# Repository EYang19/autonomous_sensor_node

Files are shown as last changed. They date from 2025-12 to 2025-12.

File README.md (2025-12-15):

# Autonomous Sensor Node Design

## Course Project – Group 6

### Team Members
- Chengyu Yang  
- Arno Liu  
- Shijia Liu  
- Zheyang Zheng  

---

## Project Overview

This project focuses on the design and implementation of **autonomous sensor nodes** capable of long-term operation using onboard power supplies. The sensor nodes are designed to independently acquire, process, and transmit sensor data, targeting applications in wearable, industrial, and medical electronics.

Two types of sensor nodes were developed in this project:
- **Photoplethysmography (PPG) Sensor Node**
- **Accelerometer (ACC) Sensor Node**

Each sensor node integrates sensing elements, power management, and a microcontroller unit (MCU) with its peripheral circuitry.

---

## Project Objectives

- Design complete sensor node hardware, including schematic and PCB layout  
- Implement low-power power management and dual-path power supply  
- Integrate MCU, sensors, and peripheral circuits  
- Verify functionality through prototype assembly and testing  
- Characterise sensor performance and validate signal acquisition  

---

## Repository Structure

```text
.
├── Datasheet_tech notes/
│   └── Datasheets and technical notes for key components
│
├── PCB_design/
│   └── Early PCB design files created using KiCad.
│       This folder contains the initial PCB design iterations
│       before the project was migrated to EasyEDA.
│
├── Final PCB Design using Easy EDA/
│   └── Finalised PCB schematics and layout designed in EasyEDA.
│       All later revisions and manufacturing-ready files are
│       maintained in this directory.
│
├── Labbook/
│   └── Laboratory notes, testing logs, and debugging records
│
├── autonomous_sensor_code/
│   └── PPGtest/
│       └── Firmware and test code for the PPG sensor node
│
├── Idea on components selection
│   └── Early design notes and rationale for component selection
│
├── ppg_processed_data.csv
│   └── Processed PPG measurement data used for analysis
│
├── README.md
│   └── Project overview and objectives
│
├── .gitattributes
│   └── Git configuration file
│
└── .DS_Store
    └── System file (can be ignored)

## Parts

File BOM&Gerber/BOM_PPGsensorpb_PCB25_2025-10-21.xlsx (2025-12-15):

No. | Quantity | Comment | Designator | Footprint | Value
1 | 2 | 2450AT18A100E | AE1,AE50 | ANT-SMD_L3.2-W1.6 |  | farnell | yes
2 | 5 | 100nF | C1,C5,C9,C10,C13 | C0603 | 100nF | farnell | yes
3 | 16 | 1uF | C3,C4,C14,C15,C19,C20,C23,C25,C52,C53,C59,C62,C64,C65,C69,C70 | C0603 | 1uF | farnell | yes
4 | 6 | 47uF | C6,C7,C27,C51,C54,C61 | C0805 | 47uF | farnell | yes
5 | 2 | 10uF | C12,C67 | C0603 | 10uF | farnell | yes
6 | 2 | 10nF | C16,C63 | C0603 | 10nF | farnell | yes
7 | 2 | 1pF | C17,C66 | C0201 | 1pF | farnell | yes
8 | 4 | 20pF | C21,C22,C56,C58 | C0603 | 20pF | farnell | yes
9 | 3 | 0Ω | C26,R14,R60 | R0603 | 0Ω | farnell | yes
10 | 5 | 100nF | C50,C55,C57,C60,C68 | C0402 | 100nF | farnell | yes
11 | 2 | B5819W-TP | D1,D50 | SOD-123_L2.8-W1.8-LS3.7-RD |  | farnell | yes
12 | 2 | PZ254V-11-04P | H1,H50 | HDR-TH_4P-P2.54-V-M |  | nonneed
13 | 2 | 2nH | L1,L50 | L0402 | 2nH | farnell | yes
14 | 2 | 3.9nH | L2,L51 | L0201 | 3.9nH | farnell | yes
15 | 2 | 2.7nH | L3,L52 | L0201 | 2.7nH | farnell | yes
16 | 1 | DNP | L4 | L0603 | tbc
17 | 6 | LTST-C190KSKT | LED1,LED2,LED3,LED50,LED51,LED52 | LED0603-RD |  | farnell | yes
18 | 2 | AO3407A | Q1,Q52 | SOT-23-3_L2.9-W1.6-P1.90-LS2.8-BR |  | alt farnell(DMG2305UX) | yes
19 | 2 | DW01 | Q2,Q51 | SOT-23-6_L2.9-W1.6-P0.95-LS2.8-BR |  | alt farnell(AP9101C) | yes
20 | 2 | 8205A | Q3,Q50 | SOT-23-6_L2.9-W1.6-P0.95-LS2.8-BR |  | digiikey | yes
21 | 14 | 10kΩ | R1,R2,R4,R7,R9,R10,R11,R50,R54,R55,R61,R62,R64,R66 | R0603 | 10kΩ | farnell | yes
22 | 2 | 100Ω | R3,R58 | R0603 | 100Ω | farnell | yes
23 | 2 | 1.5kΩ | R5,R51 | R0603 | 1.5kΩ | farnell | yes
24 | 2 | 1kΩ | R6,R52 | R0603 | 1kΩ | farnell | yes
25 | 6 | 4.7kΩ | R8,R12,R13,R59,R63,R65 | R0603 | 4.7kΩ | farnell | yes
26 | 4 | 100kΩ | R18,R19,R56,R57 | R0603 | 100kΩ | farnell | yes
27 | 2 | 3kΩ | R20,R53 | R0603 | 3kΩ | farnell | yes
28 | 2 | MSK12C02 | SW1,SW50 | SW-TH_MSK12C02 |  | farnell alt(4125522) | yes
29 | 4 | TS-1088-AR02016 | SW2,SW3,SW51,SW52 | SW-SMD_L3.9-W3.0-P4.45 |  | farnell alt(2908777) | yes
30 | 2 | MAX17048G+T10 | U1,U53 | TDFN-8_L2.0-W2.0-P0.50-BL-EP1.2 | y | farnell | yes
31 | 2 | TLV75533PDBVR | U2,U51 | SOT-23-5_L3.0-W1.7-P0.95-LS2.8-BR |  | mouser | yes
32 | 2 | TPS22917DBVR | U3,U50 | SOT-23-6_L2.9-W1.6-P0.95-LS2.8-BR |  | farnell | yes
33 | 2 | SMTU2477N-LF | U5,U54 | BAT-SMD_SMTU2477N-LF |  | mouser | yes
34 | 2 | LTC4412ES6#TRPBF | U6,U52 | TSOT-23-6_L2.9-W1.6-P0.95-LS2.8-BR |  | farnell | yes
35 | 2 | ESP32-C3FH4 | U7,U55 | QFN-32_L5.0-W5.0-P0.50-TL-EP3.7 |  | mouser | yes
36 | 2 | MAX30102EFD+T | U8,U57 | OESIP-14_L5.6-W3.3-P0.80-TL |  | farnell | yes
37 | 2 | TPS78218DDCR | U9,U56 | SOT-23-5_L3.0-W1.7-P0.95-LS2.8-BR |  |  | yes
38 | 2 | 40MHz | X1,X50 | OSC-SMD_4P-L3.2-W2.5-BL_SIT8008BI | 40MHz | farnell | yes

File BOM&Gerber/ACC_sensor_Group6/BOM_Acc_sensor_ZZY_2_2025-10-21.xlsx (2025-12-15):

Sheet: bom模板
 |  |  |  | Bill of Materials | BOM_Acc_sensor_ZZY_2_Acc_sensor_ZZY_2_2025-10-21
 |  |  |  | Project Title： | Sensor_node
 |  |  |  | Variant:
 |  |  |  | Report Time： | 2025/Oct/21 23:57:43
No. | Quantity | Comment | Designator | Footprint | Value | Manufacturer Part | Manufacturer | Supplier Part | Supplier | LCSC Price | Total
1 | 2 | 2450AT18A100E | AE1, AE2 | ANT-SMD_L3.2-W1.6 |  | 2450AT18A100E | JOHANSON(约翰逊) | C89334 | LCSC |  | #VALUE!
2 | 14 | 100nF | C1, C2, C5, C9, C10, C13, C26, C42, C43, C47, C48, C49, C50, C51 | C0603 | 100nF | CC0603KRX7R9BB104 | YAGEO(国巨) | C14663 | LCSC |  | #VALUE!
3 | 12 | 1uF | C3, C4, C14, C15, C19, C20, C34, C35, C36, C37, C38, C39 | C0603 | 1uF | CL10A105KB8NNNC | SAMSUNG(三星) | C15849 | LCSC |  | #VALUE!
4 | 6 | 47uF | C6, C7, C8, C29, C30, C31 | C0805 | 47uF | CL21A476MQYNNNE | SAMSUNG(三星) | C16780 | LCSC |  | #VALUE!
5 | 4 | 10uF | C12, C27, C44, C45 | C0603 | 10uF | CL10A106KP8NNNC | SAMSUNG(三星) | C19702 | LCSC |  | #VALUE!
6 | 2 | 10nF | C16, C32 | C0603 | 10nF | 0603B103K500NT | FH(风华) | C57112 | LCSC |  | #VALUE!
7 | 1 | 1pF | C17 | L0201 | 1pF | GRM0335C1H1R0BA01D | muRata(村田) | C85893 | LCSC |  | #VALUE!
8 | 4 | 20pF | C21, C22, C40, C41 | C0603 | 20pF | CL10C200JB8NNNC | SAMSUNG(三星) | C1648 | LCSC |  | #VALUE!
9 | 1 | 0 | C28 | C0603 | 0 | CL10A106KP8NNNC | SAMSUNG(三星) |  | LCSC |  | #VALUE!
10 | 1 | 1pF | C33 | C0201 | 1pF | GRM0335C1H1R0BA01D | muRata(村田) | C85893 | LCSC |  | #VALUE!
11 | 1 | 0Ω | C46 | C0603 | 0Ω | 0603WAF0000T5E | UNI-ROYAL(厚声) | C21189 | LCSC |  | #VALUE!
12 | 2 | B5819W-TP | D1, D2 | SOD-123_L2.8-W1.8-LS3.7-RD |  | B5819W-TP | MCC(美微科) | C84354 | LCSC |  | #VALUE!
13 | 2 | PZ254V-11-04P | H1, H2 | HDR-TH_4P-P2.54-V-M |  | PZ254V-11-04P | XFCN(兴飞) | C2691448 | LCSC |  | #VALUE!
14 | 2 | 2nH | L1, L6 | L0603 | 2nH | SDCL1608C2N0STDF | Sunlord(顺络) | C370234 | LCSC |  | #VALUE!
15 | 2 | 3.9nH | L2, L7 | L0201 | 3.9nH | LQP03HQ3N9B02D | muRata(村田) | C337939 | LCSC |  | #VALUE!
16 | 2 | 2.7nH | L3, L8 | L0201 | 2.7nH | LQP03HQ2N7B02D | muRata(村田) | C7216765 | LCSC |  | #VALUE!
17 | 1 | 0 | L4 | L0603 | 0 | SDCL1608C2N0STDF | Sunlord(顺络) |  | LCSC |  | #VALUE!
18 | 1 | Device_L | L5 | L0603 |  |  |  |  |  |  | #VALUE!
19 | 6 | LTST-C190KSKT | LED1, LED2, LED3, LED4, LED5, LED6 | LED0603-RD |  | LTST-C190KSKT | LITEON(光宝) | C125095 | LCSC |  | #VALUE!
20 | 2 | AO3407A | Q1, Q6 | SOT-23-3_L2.9-W1.6-P1.90-LS2.8-BR |  | AO3407A | AOS | C15155 | LCSC |  | #VALUE!
21 | 2 | DW01 | Q2, Q4 | SOT-23-6_L2.9-W1.6-P0.95-LS2.8-BR |  | DW01 | Hottech(合科泰) | C181096 | LCSC |  | #VALUE!
22 | 2 | 8205A | Q3, Q5 | SOT-23-6_L2.9-W1.6-P0.95-LS2.8-BR |  | 8205A | JSMSEMI(杰盛微) | C2762931 | LCSC |  | #VALUE!
23 | 14 | 10kΩ | R1, R2, R4, R7, R9, R10, R11, R27, R28, R29, R30, R31, R32, R33 | R0603 | 10kΩ | 0603WAF1002T5E | UNI-ROYAL(厚声) | C25804 | LCSC |  | #VALUE!
24 | 2 | 100Ω | R3, R24 | R0603 | 100Ω | 0603WAF1000T5E | UNI-ROYAL(厚声) | C22775 | LCSC |  | #VALUE!
25 | 2 | 1.5kΩ | R5, R25 | R0603 | 1.5kΩ | 0603WAF1501T5E | UNI-ROYAL(厚声) | C22843 | LCSC |  | #VALUE!
26 | 2 | 1kΩ | R6, R26 | R0603 | 1kΩ | 0603WAF1001T5E | UNI-ROYAL(厚声) | C21190 | LCSC |  | #VALUE!
27 | 6 | 4.7kΩ | R8, R12, R13, R34, R35, R36 | R0603 | 4.7kΩ | 0603WAF4701T5E | UNI-ROYAL(厚声) | C23162 | LCSC |  | #VALUE!
28 | 2 | 0Ω | R14, R37 | R0603 | 0Ω | 0603WAF0000T5E | UNI-ROYAL(厚声) | C21189 | LCSC |  | #VALUE!
29 | 4 | 100kΩ | R18, R19, R38, R39 | R0603 | 100kΩ | 0603WAF1003T5E | UNI-ROYAL(厚声) | C25803 | LCSC |  | #VALUE!
30 | 2 | 3kΩ | R20, R40 | R0603 | 3kΩ | 0603WAF3001T5E | UNI-ROYAL(厚声) | C4211 | LCSC |  | #VALUE!
31 | 6 | 22Ω | R21, R22, R23, R41, R42, R43 | R0603 | 22Ω | 0603WAF220JT5E | UNI-ROYAL(厚声) | C23345 | LCSC |  | #VALUE!
32 | 2 | MSK12C02 | SW1, SW4 | SW-TH_MSK12C02 |  | MSK12C02 | SHOU HAN(首韩) | C431540 | LCSC |  | #VALUE!
33 | 4 | TS-1088-AR02016 | SW2, SW3, SW5, SW6 | SW-SMD_L3.9-W3.0-P4.45 |  | TS-1088-AR02016 | XUNPU(讯普) | C720477 | LCSC |  | #VALUE!
34 | 2 | MAX17048G+T10 | U1, U10 | TDFN-8_L2.0-W2.0-P0.50-BL-EP1.2 |  | MAX17048G+T10 | ADI(亚德诺)/MAXIM(美信) | C2682616 | LCSC |  | #VALUE!
35 | 2 | TLV75533PDBVR | U2, U13 | SOT-23-5_L3.0-W1.7-P0.95-LS2.8-BR |  | TLV75533PDBVR | TI(德州仪器) | C404027 | LCSC |  | #VALUE!
36 | 2 | TPS22917DBVR | U3, U12 | SOT-23-6_L2.9-W1.6-P0.95-LS2.8-BR |  | TPS22917DBVR | TI(德州仪器) | C2681320 | LCSC |  | #VALUE!
37 | 2 | LIS2DE12TR | U4, U8 | LGA-12_L2.0-W2.0-P0.50-BL |  | LIS2DE12TR | ST(意法半导体) | C155639 | LCSC |  | #VALUE!
38 | 2 | SMTU2477N-LF | U5, U9 | BAT-SMD_SMTU2477N-LF |  | SMTU2477N-LF | RENATA(瑞纳达) | C3029193 | LCSC |  | #VALUE!
39 | 2 | LTC4412ES6#TRPBF | U6, U11 | TSOT-23-6_L2.9-W1.6-P0.95-LS2.8-BR |  | LTC4412ES6#TRPBF | ADI(亚德诺) | C514442 | LCSC |  | #VALUE!
40 | 1 | ESP32-C3 | U7 | QFN-32_L5.0-W5.0-P0.50-TL-EP3.7 |  | ESP32-C3 | ESPRESSIF(乐鑫) | C2838500 | LCSC |  | #VALUE!
41 | 1 | ESP32-C3FH4 | U14 | QFN-32_L5.0-W5.0-P0.50-TL-EP3.7 |  | ESP32-C3FH4 | ESPRESSIF(乐鑫) | C2858491 | LCSC |  | #VALUE!
42 | 2 | 40MHz | X1, X2 | OSC-SMD_4P-L3.2-W2.5-BL_SIT8008BI | 40MHz | X322540MPB4SI | YXC(扬兴晶振) | C9010 | LCSC |  | #VALUE!
43 | #VALUE!

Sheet: Field汇总
Project Title | Sensor_node
Borard Title | Acc_sensor_ZZY_2
Schematic Title | Acc_sensor_ZZY_2
PCB Title
Variant Name
Total Quantity | 134
Report Time | 23:57:43
Report Date | 2025年10月21日
Report Date&Time | 2025年10月21日 23:57:43
File Name | BOM_Acc_sensor_ZZY_2_Acc_sensor_ZZY_2_2025-10-21
Filter Option | Add into BOM:no;

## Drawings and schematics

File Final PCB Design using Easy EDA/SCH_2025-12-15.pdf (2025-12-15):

# Power Management

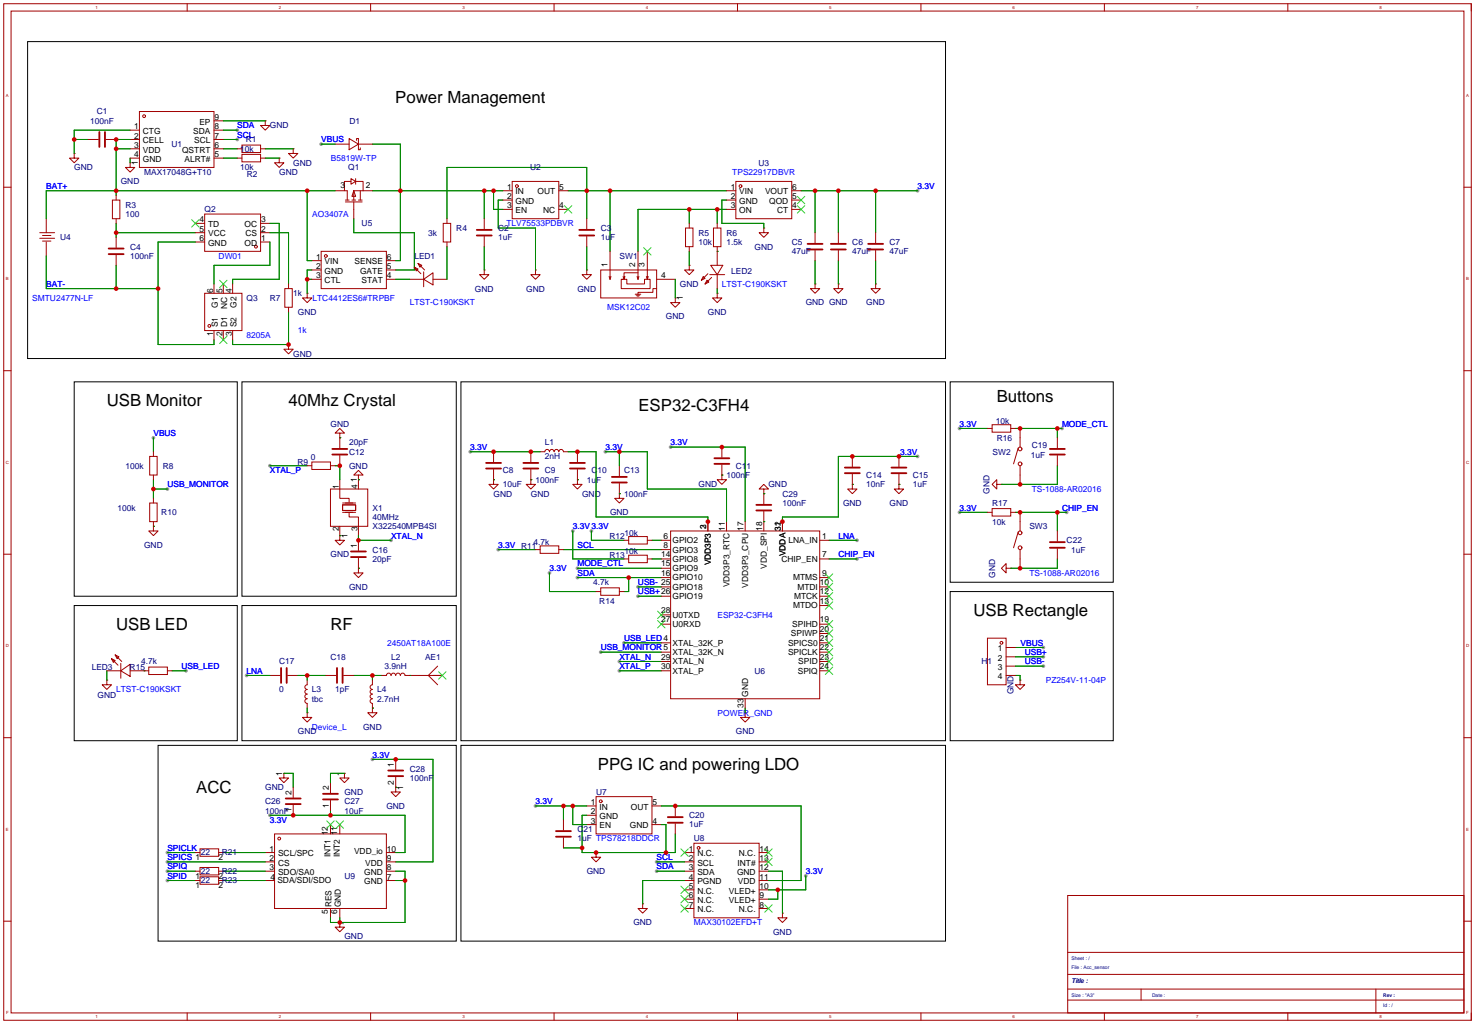
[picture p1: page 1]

PPG IC and powering LDO

VLED+ 10 VDD 11 GND 12 INT# 13 N.C. 14

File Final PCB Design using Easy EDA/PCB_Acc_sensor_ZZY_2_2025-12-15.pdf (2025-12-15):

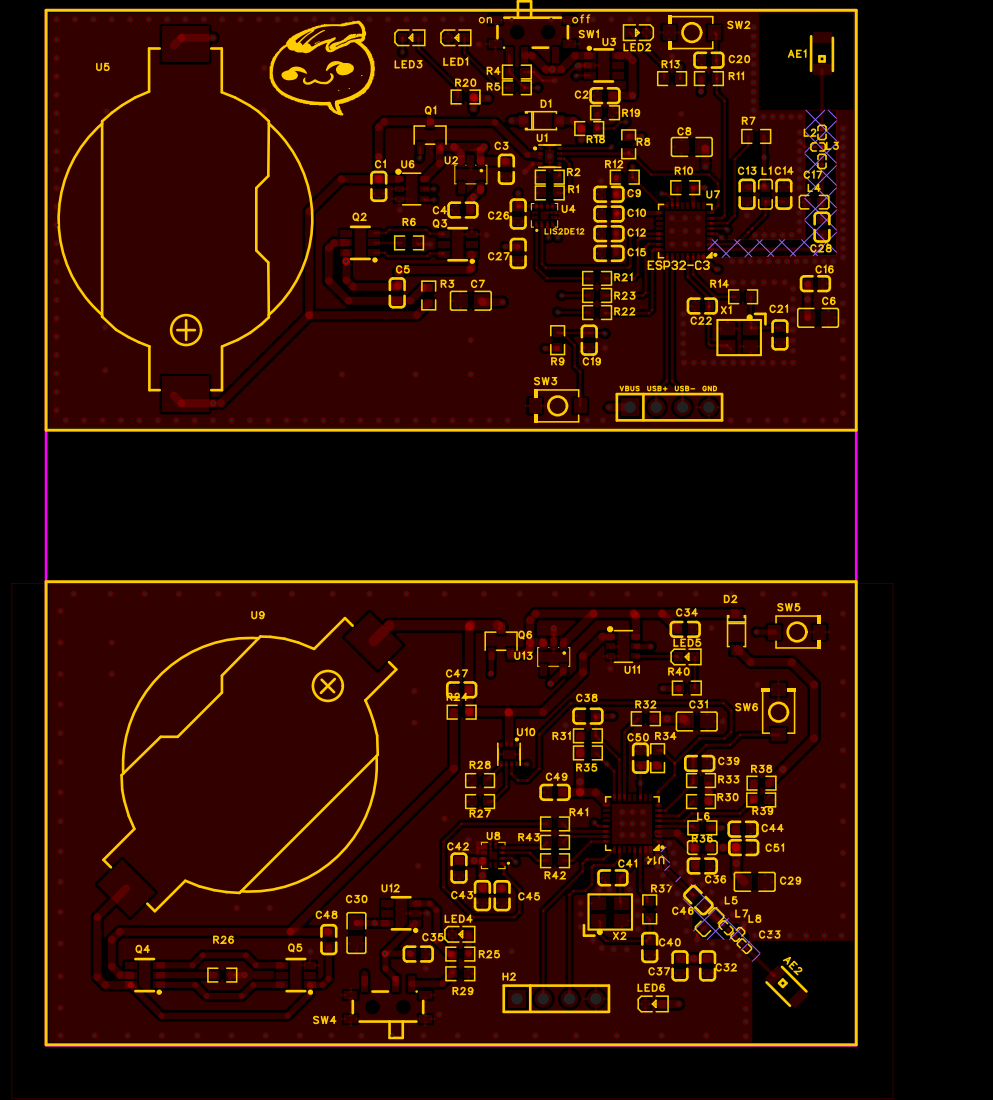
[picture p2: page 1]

VBUS USB+ USB- GND

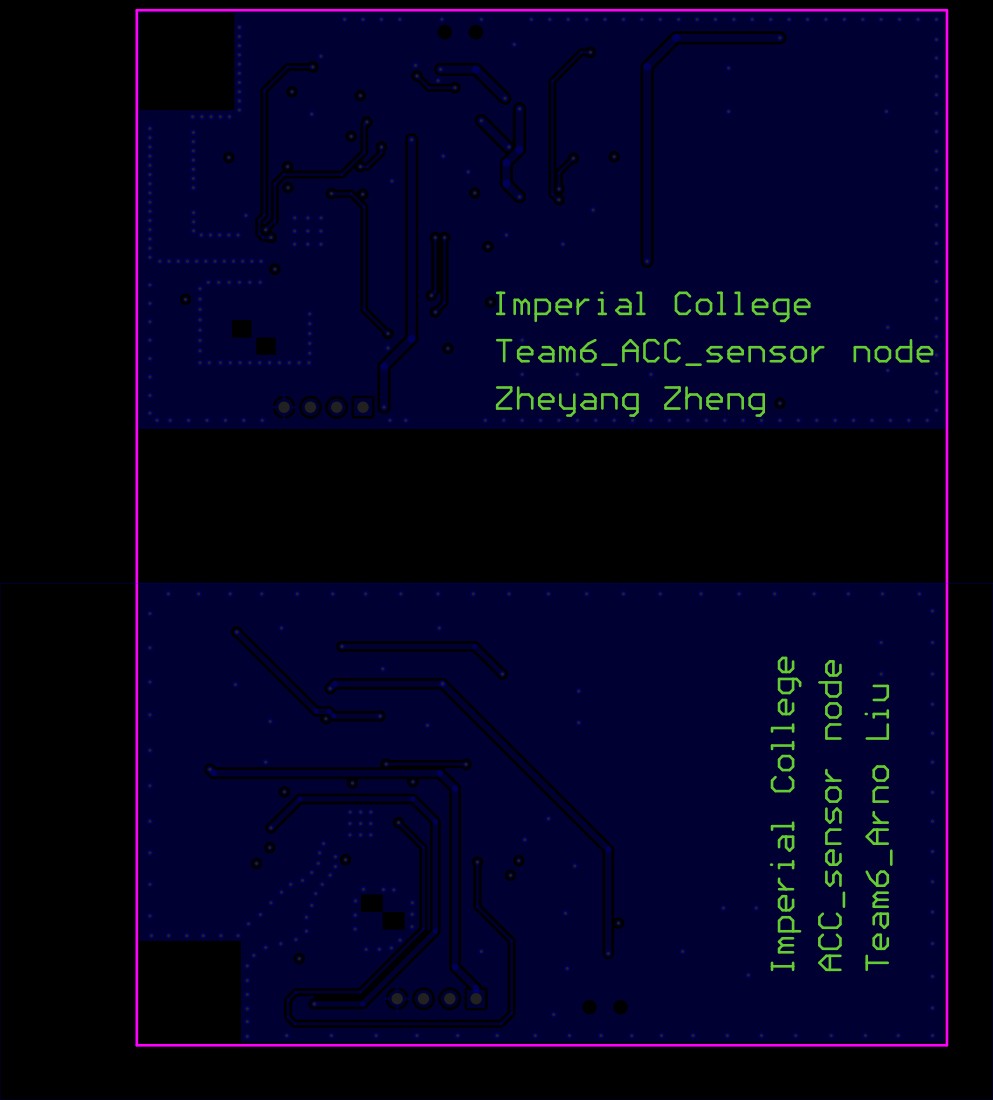
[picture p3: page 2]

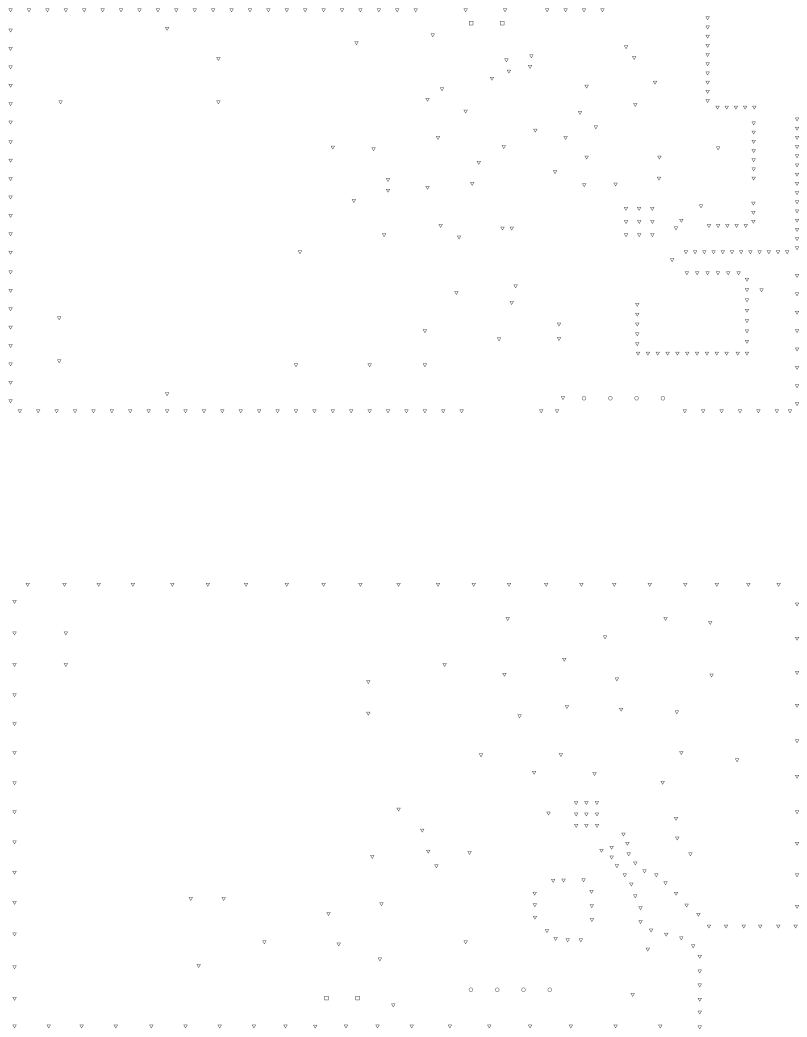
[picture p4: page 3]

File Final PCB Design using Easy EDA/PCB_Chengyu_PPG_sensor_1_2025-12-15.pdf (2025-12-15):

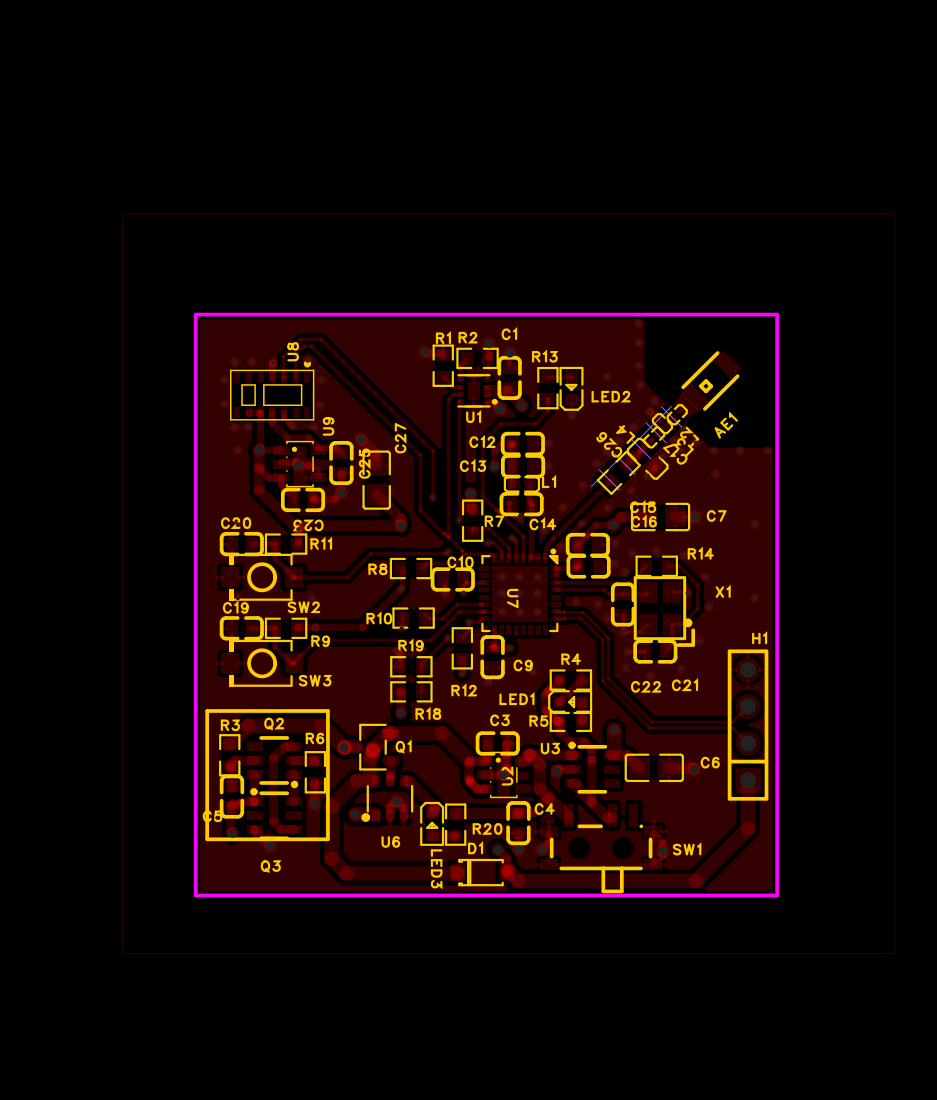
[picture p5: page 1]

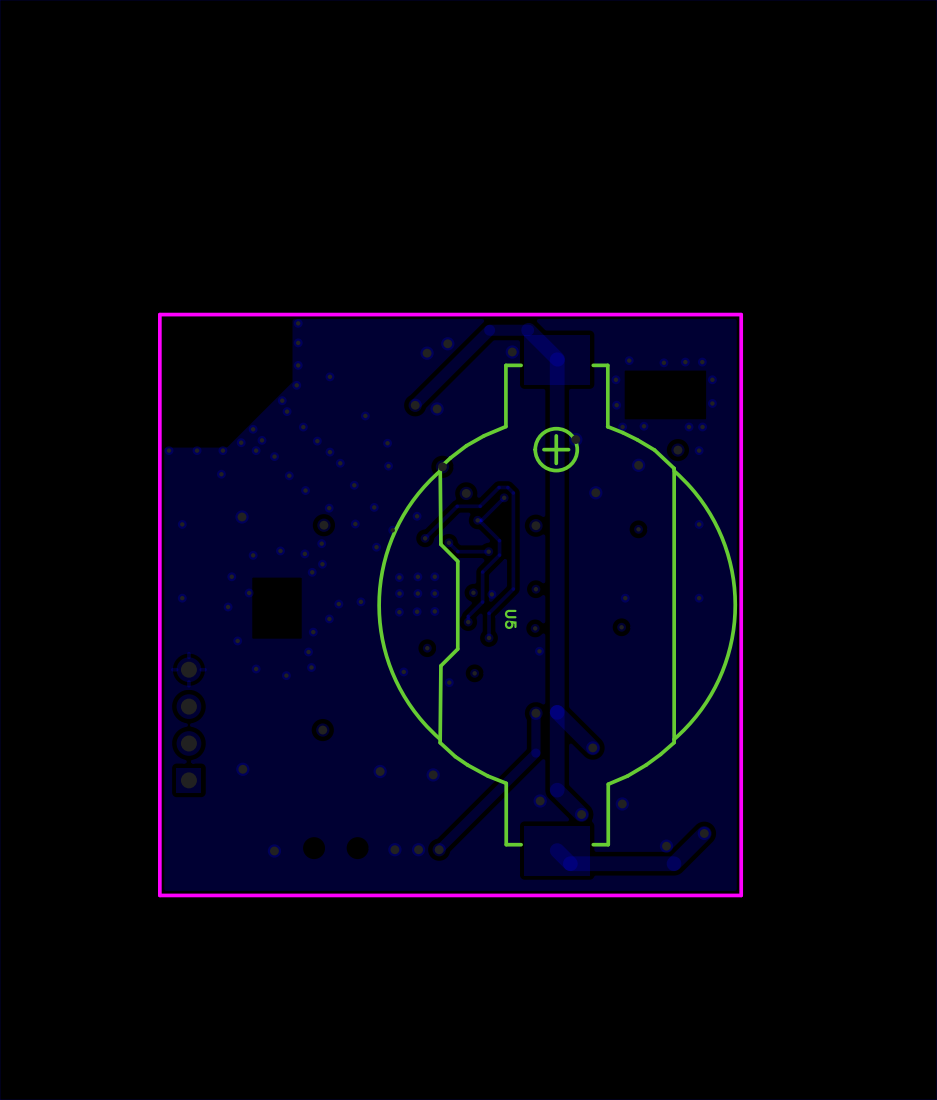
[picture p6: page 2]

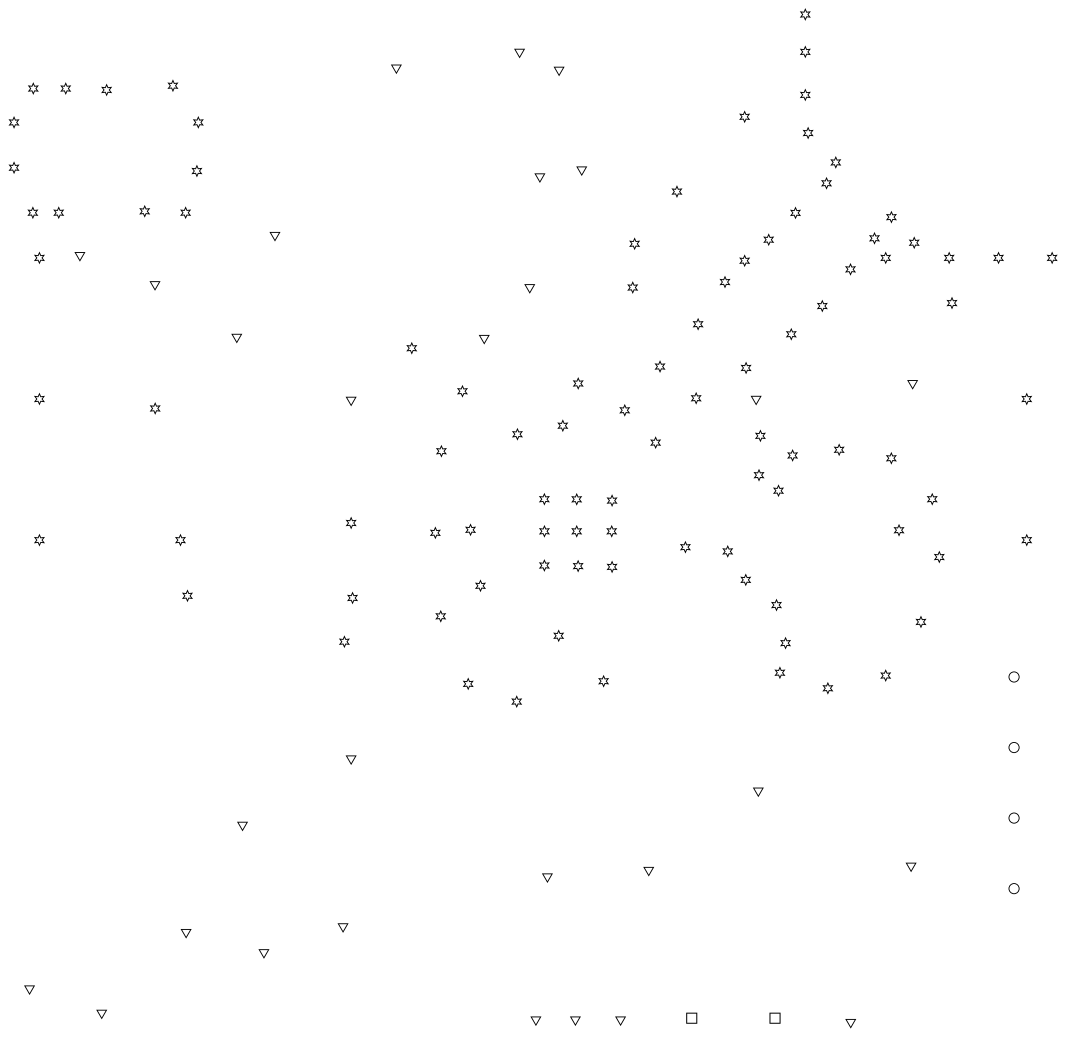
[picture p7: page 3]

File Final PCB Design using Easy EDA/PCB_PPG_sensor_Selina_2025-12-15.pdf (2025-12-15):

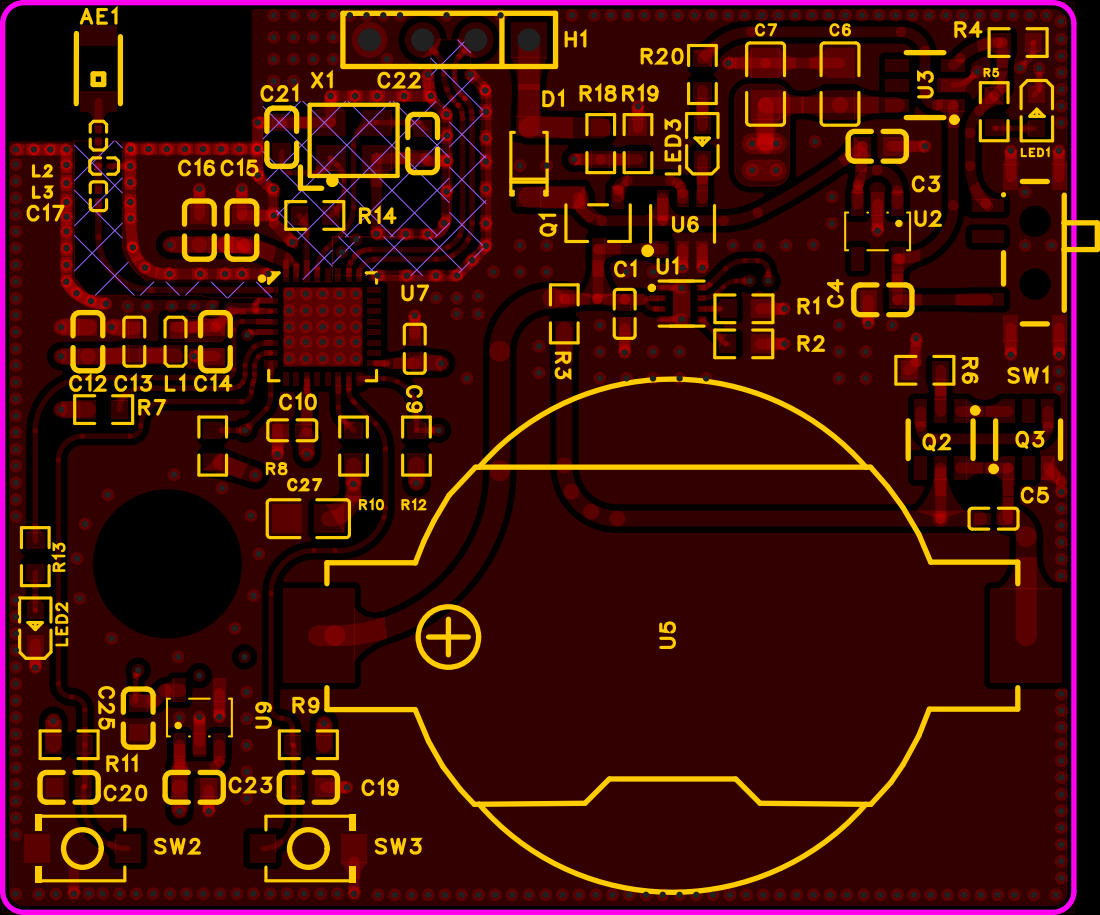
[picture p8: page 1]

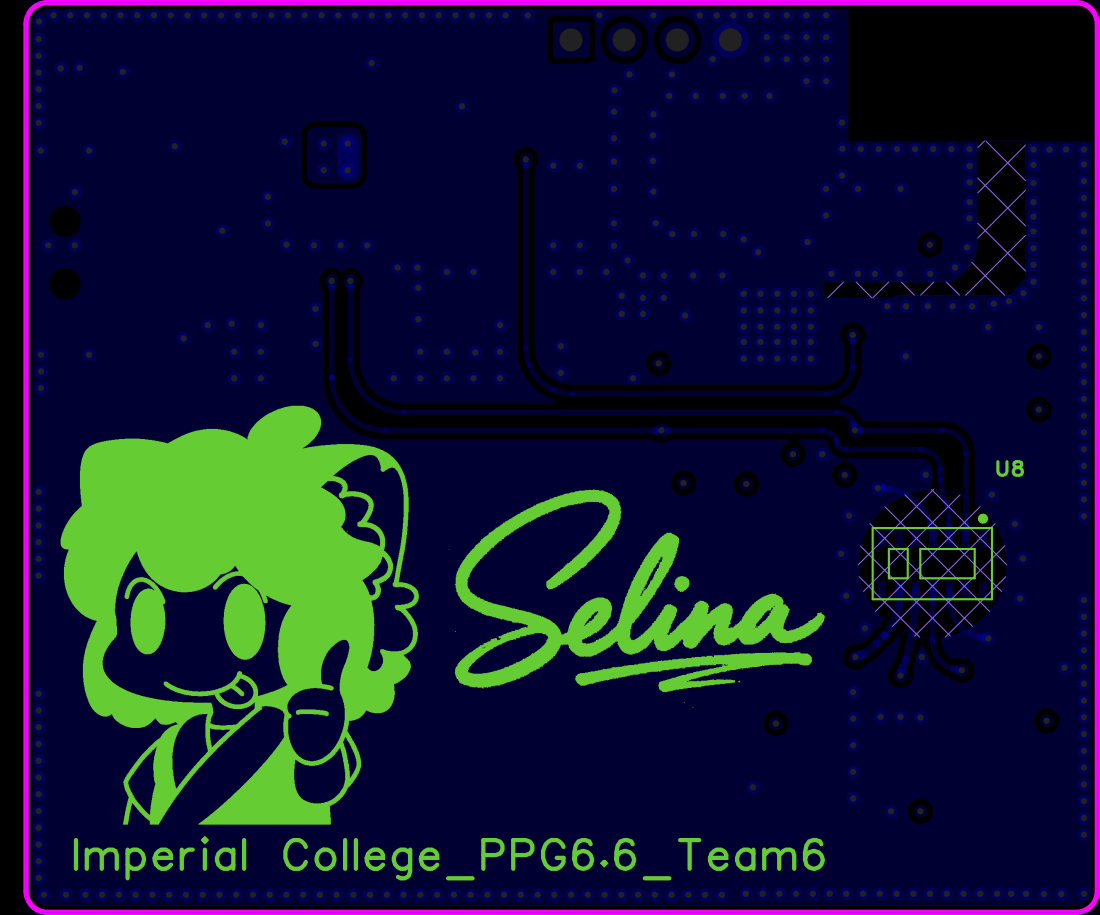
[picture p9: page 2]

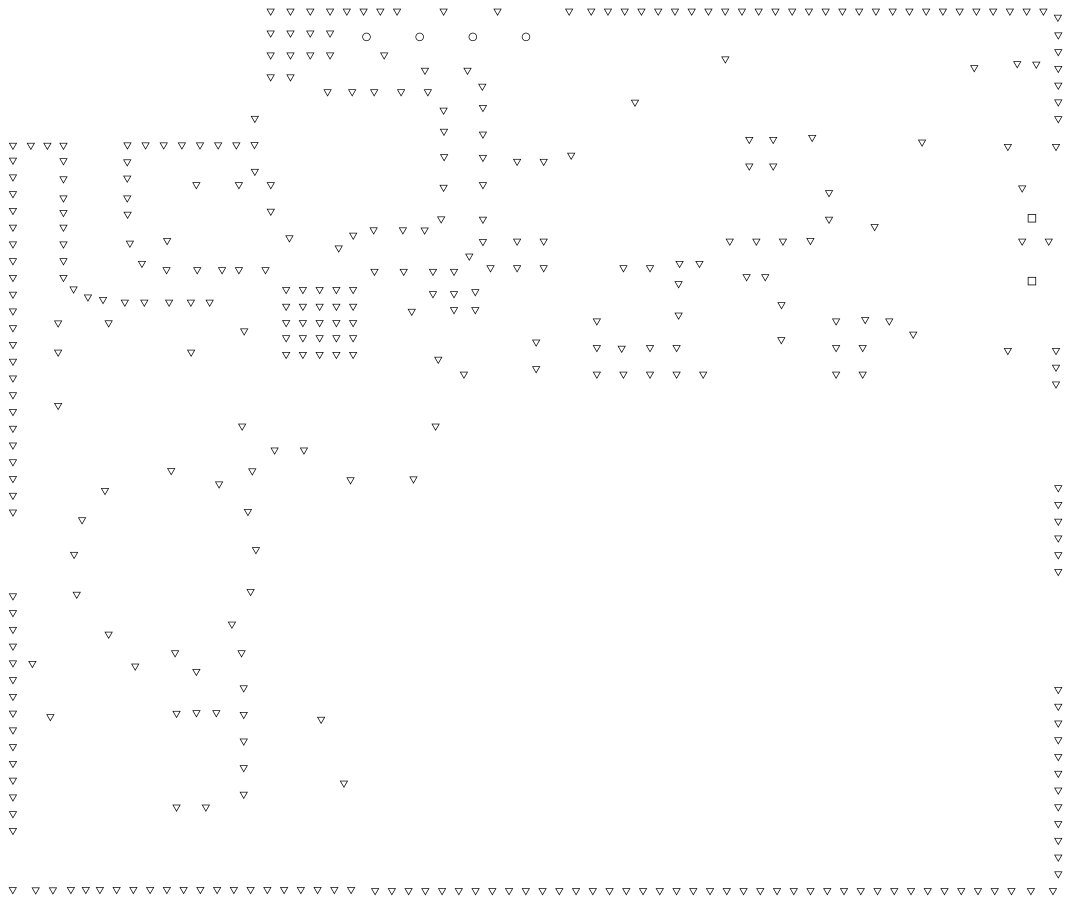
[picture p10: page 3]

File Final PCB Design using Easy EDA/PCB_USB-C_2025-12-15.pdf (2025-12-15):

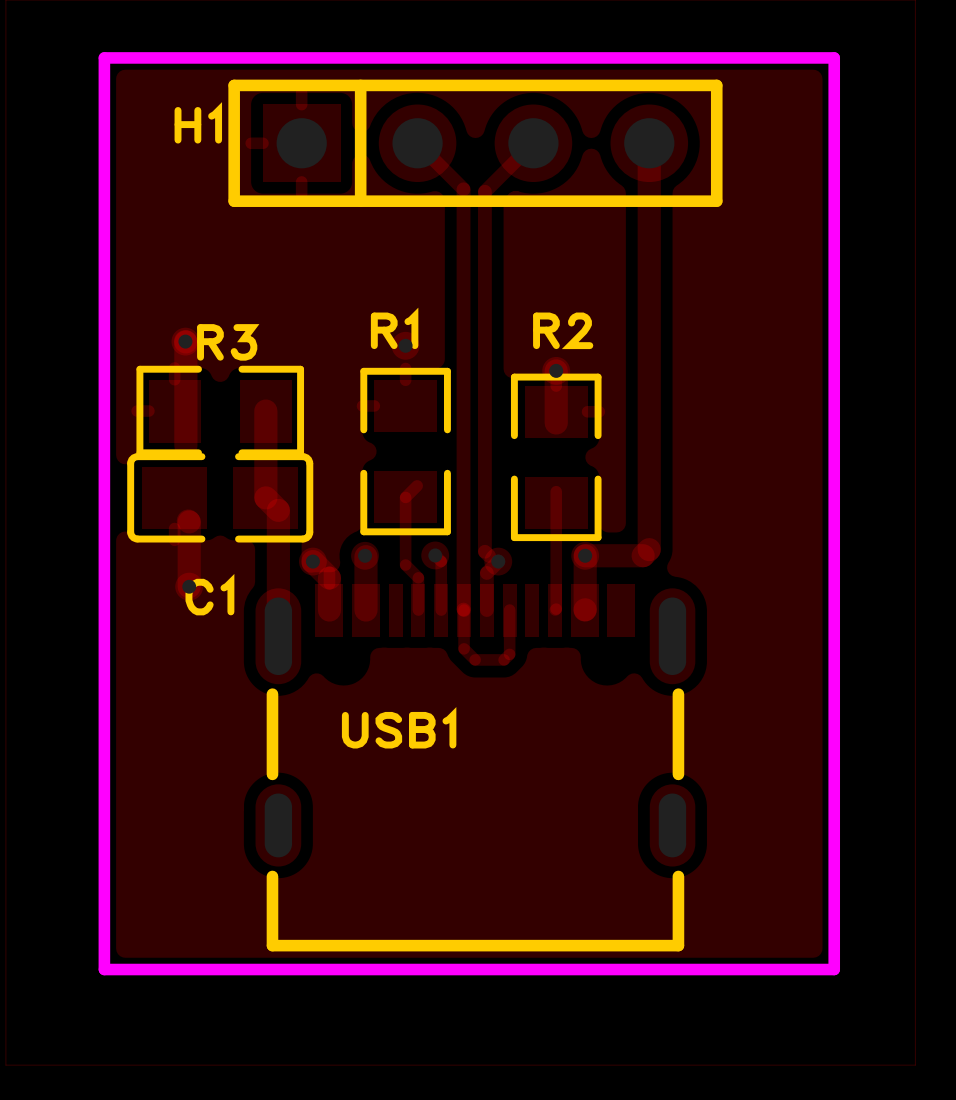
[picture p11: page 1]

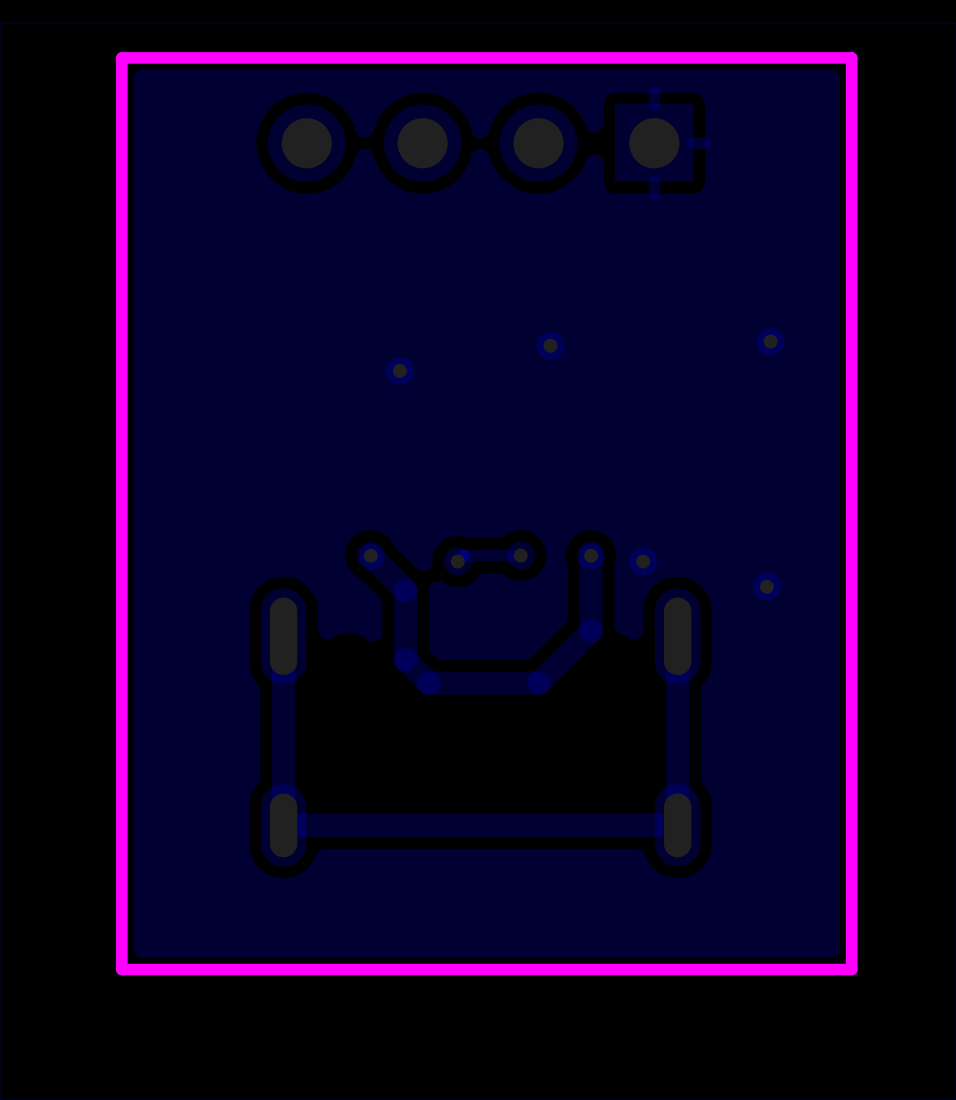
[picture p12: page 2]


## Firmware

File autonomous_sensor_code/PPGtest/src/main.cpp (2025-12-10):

#include <Arduino.h>
#include <Wire.h>
#include <math.h>

// ==== 新增：BLE 相关头文件 ====
#include <BLEDevice.h>
#include <BLEUtils.h>
#include <BLEServer.h>

// ===== I2C 引脚：GPIO8=SCL, GPIO10=SDA =====
static const int I2C_SDA = 10;
static const int I2C_SCL = 3;
static const uint32_t I2C_FREQ = 400000;

static const uint8_t MAX30102_ADDR = 0x57;

// Registers
static const uint8_t REG_INTR_STATUS_1 = 0x00;
static const uint8_t REG_INTR_STATUS_2 = 0x01;
static const uint8_t REG_INTR_ENABLE_1 = 0x02;
static const uint8_t REG_INTR_ENABLE_2 = 0x03;
static const uint8_t REG_FIFO_WR_PTR   = 0x04;
static const uint8_t REG_OVF_COUNTER   = 0x05;
static const uint8_t REG_FIFO_RD_PTR   = 0x06;
static const uint8_t REG_FIFO_DATA     = 0x07;
static const uint8_t REG_FIFO_CONFIG   = 0x08;
static const uint8_t REG_MODE_CONFIG   = 0x09;
static const uint8_t REG_SPO2_CONFIG   = 0x0A;
static const uint8_t REG_LED1_PA       = 0x0C; // RED
static const uint8_t REG_LED2_PA       = 0x0D; // IR
static const uint8_t REG_MULTI_LED_CTRL1 = 0x11;
static const uint8_t REG_MULTI_LED_CTRL2 = 0x12;
static const uint8_t REG_REV_ID        = 0xFE;
static const uint8_t REG_PART_ID       = 0xFF;

// ==== 新增：BLE UUID 与名称（可按需改自己的 UUID） ====
#define SERVICE_UUID        "d3aa6a66-a623-4c76-80a5-a66004acf0bf"
#define CHARACTERISTIC_UUID "2df03c7d-8ac5-493e-9d88-ac467aed4ad0"
#define BLE_SERVER_NAME     "ppg"

// ==== 新增：BLE 全局对象 ====
BLEServer*        pServer        = nullptr;
BLECharacteristic* pCharacteristic = nullptr;
bool deviceConnected = false;

// ==== 新增：BLE 回调 ====
class ServerCallbacks : public BLEServerCallbacks {
  void onConnect(BLEServer* pServer) override {
    deviceConnected = true;
    Serial.println("[BLE] Central connected");
  }
  void onDisconnect(BLEServer* pServer) override {
    deviceConnected = false;
    Serial.println("[BLE] Central disconnected, restart advertising");
    pServer->startAdvertising();
  }
};

// --- I2C helpers ---
static bool i2cWrite8(uint8_t reg, uint8_t val) {
  Wire.beginTransmission(MAX30102_ADDR);
  Wire.write(reg);
  Wire.write(val);
  return (Wire.endTransmission() == 0);
}

static bool i2cRead8(uint8_t reg, uint8_t &val) {
  Wire.beginTransmission(MAX30102_ADDR);
  Wire.write(reg);
  if (Wire.endTransmission(false) != 0) return false;
  if (Wire.requestFrom((int)MAX30102_ADDR, 1) != 1) return false;
  val = Wire.read();
  return true;
}

static bool i2cReadBytes(uint8_t reg, uint8_t *buf, size_t len) {
  Wire.beginTransmission(MAX30102_ADDR);
  Wire.write(reg);
  if (Wire.endTransmission(false) != 0) return false;
  if (Wire.requestFrom((int)MAX30102_ADDR, (int)len) != (int)len) return false;
  for (size_t i = 0; i < len; i++) buf[i] = Wire.read();
  return true;
}

static bool max30102Init() {
  uint8_t part = 0, rev = 0;
  if (!i2cRead8(REG_PART_ID, part) || !i2cRead8(REG_REV_ID, rev)) {
    Serial.println("MAX30102: I2C read failed.");
    return false;
  }
  Serial.print("MAX30102 PartID=0x"); Serial.print(part, HEX);
  Serial.print(" RevID=0x"); Serial.println(rev, HEX);

  // Reset
  i2cWrite8(REG_MODE_CONFIG, 0x40);
  delay(50);

  // Disable interrupts (polling)
  i2cWrite8(REG_INTR_ENABLE_1, 0x00);
  i2cWrite8(REG_INTR_ENABLE_2, 0x00);

  // FIFO: sample avg=4, rollover=1
  i2cWrite8(REG_FIFO_CONFIG, (0b010 << 5) | (1 << 4) | 0x00);

  // Mode: SpO2 (RED+IR)
  i2cWrite8(REG_MODE_CONFIG, 0x03);

  // SPO2 config: range=4096nA, 100sps, 18bit
  i2cWrite8(REG_SPO2_CONFIG, (0b01 << 5) | (0b001 << 2) | 0b11);

  // LED currents
  i2cWrite8(REG_LED1_PA, 0x24); // RED
  i2cWrite8(REG_LED2_PA, 0x24); // IR

  // SLOT1=RED, SLOT2=IR
  i2cWrite8(REG_MULTI_LED_CTRL1, (0b010 << 4) | 0b001);
  i2cWrite8(REG_MULTI_LED_CTRL2, 0x00);

  // Clear FIFO pointers
  i2cWrite8(REG_FIFO_WR_PTR, 0x00);
  i2cWrite8(REG_OVF_COUNTER, 0x00);
  i2cWrite8(REG_FIFO_RD_PTR, 0x00);

  // Clear pending status
  uint8_t s1, s2;
  i2cRead8(REG_INTR_STATUS_1, s1);
  i2cRead8(REG_INTR_STATUS_2, s2);

  Serial.println("MAX30102 init done.");
  return true;
}

static int max30102AvailableSamples() {
  uint8_t wr = 0, rd = 0;
  if (!i2cRead8(REG_FIFO_WR_PTR, wr)) return 0;
  if (!i2cRead8(REG_FIFO_RD_PTR, rd)) return 0;
  return (int)((wr - rd) & 0x1F); // 5-bit ring
}

static bool max30102ReadSample(uint32_t &red, uint32_t &ir) {
  uint8_t buf[6];
  if (!i2cReadBytes(REG_FIFO_DATA, buf, 6)) return false;

  uint32_t r = ((uint32_t)buf[0] << 16) | ((uint32_t)buf[1] << 8) | buf[2];
  uint32_t i = ((uint32_t)buf[3] << 16) | ((uint32_t)buf[4] << 8) | buf[5];

  red = (r & 0x3FFFF); // 18-bit
  ir  = (i & 0x3FFFF);
  return true;
}

/* ======================== 信号处理 + HR/SpO2 ======================== */

const int SAMPLE_RATE_HZ = 100;

// IIR 状态
static float redDC   = 0.0f;
static float irDC    = 0.0f;
static float redAcF  = 0.0f;
static float irAcF   = 0.0f;
static float redAcSq = 0.0f;
static float irAcSq  = 0.0f;
static float irAbsMean = 0.0f;

// IIR 参数
const float DC_ALPHA      = 0.02f;
const float LP_ALPHA      = 0.20f;
const float RMS_ALPHA     = 0.05f;
const float MEANABS_ALPHA = 0.03f;

// 阈值范围（基础值）
const float THRESH_MIN_BASE = 20.0f;
const float THRESH_MAX      = 800.0f;

// 手指状态 & 时间
static bool   fingerActive        = false;
static unsigned long fingerActiveStartMs = 0;

// 前 5s：1s 预热 + 4s 区间累计
const unsigned long WARMUP_MS           = 1000;  // 第 1 s 只收敛 IIR
const unsigned long INITIAL_TOTAL_MS    = 5000;  // 接触后前 5 s 属于“初始阶段”
const unsigned long INIT_INTERVAL_MS    = 4000;  // 从“第一次峰”起累计的 4s 区间

// 初始区间统计（从第一次峰算起 4s）
static bool   initPhase        = false;
static unsigned long initFirstBeatMs = 0;
static unsigned int  initBeatCount   = 0;

// 预热状态
static bool warmup      = false;
static unsigned long warmupEndMs = 0;

// 手指接触判定
const uint32_t SIG_ON_THRESHOLD  = 100000;
const uint32_t SIG_OFF_THRESHOLD = 80000;

// 滑动窗口用的脉搏时间戳（用于 5s/2s HR）
static unsigned long pulseTimes[32];
static int pulseWriteIndex = 0;
static int pulseStored     = 0;

// 峰检测状态
static float prev2 = 0.0f, prev1 = 0.0f;
static unsigned long lastPulseMs = 0;

// beat-to-beat HR（供 5s 后使用）
static unsigned long lastBeatMs   = 0;
static float hrFast               = 0.0f;
static bool hrFastValid           = false;
static unsigned long hrFastTimeMs = 0;

// 输出值
static float lastHeartRate = 0.0f;
static float lastSpO2      = 0.0f;
static uint32_t lastRawRed = 0;
static uint32_t lastRawIr  = 0;

// --- 显示层小窗口平滑（UI 层，3 点均值） ---
static float hrDisplayBuf[3] = {0};  // 最近 3 次 HR
static int   hrDisplayCount  = 0;    // 有效个数
static int   hrDisplayIndex  = 0;    // 环形写指针

// 滑动窗口
const unsigned long HR_WINDOW_LONG_MS  = 5000;  // 5s
const unsigned long HR_WINDOW_SHORT_MS = 2000;  // 2s

// 不应期
const unsigned long REFRACTORY_MS = 350;

// HR 限速
const float HR_STEP_LIMIT_INIT = 80.0f;  // 前 5 秒
const float HR_STEP_LIMIT_NORM = 40.0f;  // 5 秒之后

static void resetInitPhase() {
  initPhase        = false;
  initFirstBeatMs  = 0;
  initBeatCount    = 0;
}

// 注册脉搏到滑动窗口（预热结束后就可以）
static void registerPulse(unsigned long t_ms) {
  if (!fingerActive || warmup) return;
  pulseTimes[pulseWriteIndex] = t_ms;
  pulseWriteIndex = (pulseWriteIndex + 1) % 32;
  if (pulseStored < 32) pulseStored++;
}

// 计算 HR（与你原来的版本一致）
static void computeHeartRate(unsigned long nowMs) {
  if (!fingerActive) {
    lastHeartRate = 0.0f;
    pulseStored   = 0;
    hrFastValid   = false;
    resetInitPhase();
    return;
  }

  unsigned long contactDuration = nowMs - fingerActiveStartMs;

  // 预热期：不输出 HR
  if (warmup) {
    lastHeartRate = 0.0f;
    return;
  }

  bool inInitialTime = (contactDuration < INITIAL_TOTAL_MS);
  float hrNew = 0.0f;

  // ================== 接触后前 5 秒 ==================
  if (inInitialTime) {
    // 使用“从第一次峰起的 4s 区间累计均值”
    if (initPhase) {
      unsigned long intervalMs = nowMs - initFirstBeatMs;
      if (intervalMs > 0 && intervalMs <= INIT_INTERVAL_MS && initBeatCount >= 2) {
        float durSec = intervalMs / 1000.0f;
        hrNew = (float)initBeatCount * 60.0f / durSec;
      } else if (intervalMs > INIT_INTERVAL_MS) {
        // 超过 4s 就结束初始区间，后面进正常逻辑
        resetInitPhase();
      }
    }

    // 区间均值无效，就先不更新 HR（保持上一次）
    if (hrNew <= 0.0f || hrNew < 30.0f || hrNew > 220.0f) {
      return;
    }

    // 前 5 秒：无平滑，只限速 80
    if (lastHeartRate <= 0.0f) {
      lastHeartRate = hrNew;  // 冷启动
    } else {
      float diff = hrNew - lastHeartRate;
      if (diff > HR_STEP_LIMIT_INIT)  diff = HR_STEP_LIMIT_INIT;
      if (diff < -HR_STEP_LIMIT_INIT) diff = -HR_STEP_LIMIT_INIT;
      lastHeartRate += diff;          // 直接走过去，不做平均
    }
    return;
  }

  // ================== 5 秒之后：滑动窗口 + 权重 ==================
  // 此时初始区间结束，不再用累计平均
  if (initPhase) {
    resetInitPhase();
  }

  // 统计滑动窗口
  int countLong  = 0;
  int countShort = 0;
  for (int i = 0; i < pulseStored; ++i) {
    unsigned long dt = nowMs - pulseTimes[i];
    if (dt <= HR_WINDOW_LONG_MS)  countLong++;
    if (dt <= HR_WINDOW_SHORT_MS) countShort++;
  }

  float hrLong  = 0.0f;
  float hrShort = 0.0f;

  if (countLong >= 2) {
    hrLong = (float)countLong * 60.0f / (HR_WINDOW_LONG_MS / 1000.0f);
  }
  if (countShort >= 2) {
    hrShort = (float)countShort * 60.0f / (HR_WINDOW_SHORT_MS / 1000.0f);
  }

  // beat-to-beat 快 HR，最近 5 秒内有效
  float hrFastUse = 0.0f;
  bool fastFresh  = false;
  if (hrFastValid && (nowMs - hrFastTimeMs) <= 5000) {
    hrFastUse = hrFast;
    fastFresh = true;
  }

  // 老方法：fast + long 加权
  if (hrLong > 0.0f && fastFresh) {
    if (contactDuration < 10000) {
      hrNew = 0.5f * hrFastUse + 0.5f * hrLong;     // 5–10 s：fast 权重大一点
    } else {
      hrNew = 0.3f * hrFastUse + 0.7f * hrLong;     // 10 s 后：偏重 long 稳定
    }
  } else if (hrLong > 0.0f) {
    hrNew = hrLong;
  } else if (fastFresh) {
    hrNew = hrFastUse;
  } else {
    // 没有新 HR：保持旧值，不归零
    return;
  }

  // 合理区间
  if (hrNew <= 0.0f || hrNew < 30.0f || hrNew > 220.0f) {
    return;
  }

  // 5 秒后：限速 40 + 平滑
  if (lastHeartRate <= 0.0f) {
    lastHeartRate = hrNew;
  } else {
    float diff = hrNew - lastHeartRate;
    if (diff > HR_STEP_LIMIT_NORM)  diff = HR_STEP_LIMIT_NORM;
    if (diff < -HR_STEP_LIMIT_NORM) diff = -HR_STEP_LIMIT_NORM;
    float candidate = lastHeartRate + diff;
    lastHeartRate = 0.5f * lastHeartRate + 0.5f * candidate;
  }
}
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

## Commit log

2025-10-08 First moving files into Repository
    [Acc_sensor.kicad_pcb, Acc_sensor.kicad_sch, cf170ec05ef97a900aad31853f6432f8.kicad_pcb, d63e7b53e30aa773d97971d4b1bd02d4.kicad_sch]
2025-10-09 upload file
    split into acc sensor and BMS file. Yet to copy to have a ppg sensor file
    [Acc_sensor.kicad_sch, BMS.kicad_pcb, BMS.kicad_sch]
2025-10-09 integrated BMS back into main schematic
    [Acc_sensor.kicad_sch]
2025-10-10 update
    update yesterday group work
    [Acc_sensor.kicad_sch]
2025-10-10 modify
    chipenable, I2C pullup, RC value comfirmed.
    [Acc_sensor.kicad_sch]
2025-10-13 Split into two sensor file
    split into ppg and acc file. draw the rect for better view. next to do is design usb/battery power adaption
    [PPG_sensor_node.kicad_pcb, PPG_sensor_node.kicad_sch]
2025-10-13 update
    choose a appropriate fuel gauge and draw the correspond symbol to add it into power management system for both two pcb file
    [Acc_sensor.kicad_sch, PPG_sensor_node.kicad_sch]
2025-10-13 update
    add the ceramic parallel capacitor for driving ESP32 at big current
    [Acc_sensor.kicad_sch, PPG_sensor_node.kicad_sch]
2025-11-20 第一版accppg码
2025-12-14 ppg data
    [ppg_processed_data.csv]
2025-12-15 Upload PCB design
    This is the final design using Easy EDA
2025-12-15 Create README.md for project overview and objectives
    Added initial README for Autonomous Sensor Node project.
2025-12-15 Add BOM and Gerber file for PCB
    [BOM_Acc_sensor_ZZY_2_2025-10-21.xlsx, BOM_PPGsensorpb_PCB25_2025-10-21.xlsx, PickAndPlace_Acc_sensor_ZZY_2_2025-10-22.xlsx, PickAndPlace_PCB25_2025-10-21.xlsx]
